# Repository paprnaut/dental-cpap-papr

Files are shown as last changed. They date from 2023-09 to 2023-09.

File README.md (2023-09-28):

# Dental CPAP PAPR

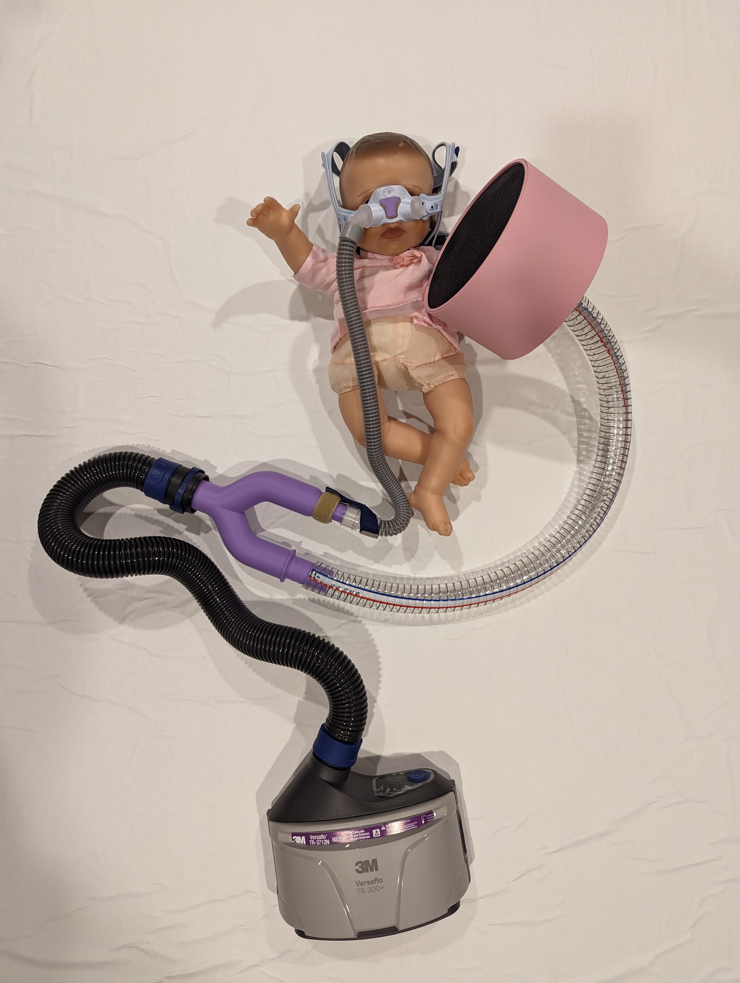
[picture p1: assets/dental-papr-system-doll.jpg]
System photo

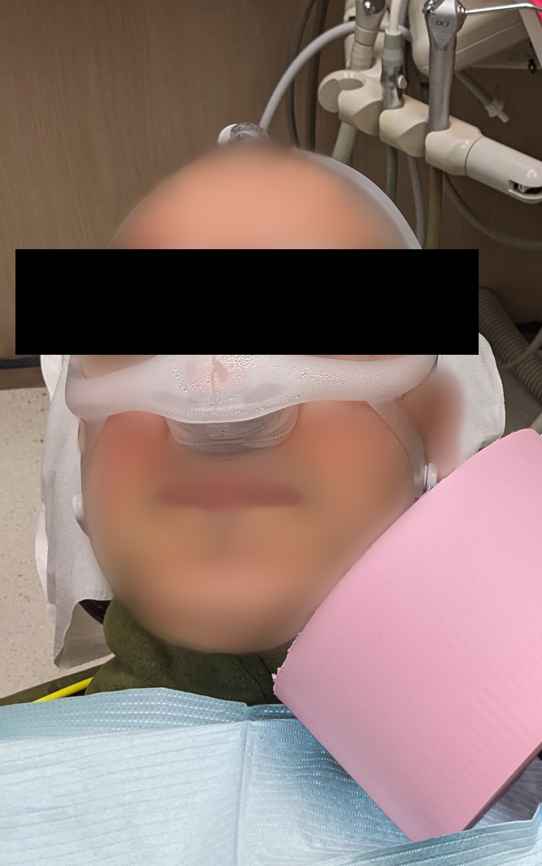
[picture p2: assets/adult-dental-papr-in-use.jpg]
In use photo photo


***Important Disclaimer: This is a prototype device, offered free-of-charge as a public service, and no claim, guarantee, or warranty of performance or suitablity for any purpose is offered or implied.  This device has not been independently certified or approved.  Use of this design or any derivatives thereof is entirely at your own risk.  By using any of these materials, you acknowledge that you have read and understood the Disclaimer at the end of this document.  Please do not use these materials if you do not understand and accept these risks.***

## Bill of Materials

**Printed Parts**
| Item | Quantity | Notes |
| ---- | -------- | ----- |
| Dental PAPR - Child CPAP Hole Plug.stl | 1 | To plug holes in Pixi nasal pad. Print for child version only. |
| Dental PAPR - LaminarNozzleBody-Wide.stl | 1 | Handheld wand to blow clean air over the mouth and face. |
| Dental PAPR - LaminarNozzleFitting-Female-Short.stl | 1 | Nut for handheld wand. |
| Dental PAPR - LaminarNozzleFitting-Short.stl | 1 | Hose fitting for handheld wand. |
| Dental PAPR - MeshHolderSpacer-Wide.stl | 2 | Hoop frames. Glue screen door material onto these to hold straws in place. |
| Dental PAPR - NozzleFlowReducer d0,50.stl | 1 | Part with 0,5" opening inserts into hose fitting on Y-splitter to reduce flow to the handheld wand to improve flow to the CPAP. Tested for adult version only. |
| Dental PAPR - TR300 Y Adapter - Adult.stl | 1 | Y-splitter / adapter. Print for adult version only. |
| Dental PAPR - TR300 Y Adapter - Child.stl | 1 | Y-splitter / adapter. Print for child version only. |
| Dental PAPR - v1 tr300 y-splitter.3mf | 1 | Y-splitter / adapter for v1 with adjustable valves only. |
| Dental PAPR - v1 1in pipe to CPAP adapter.3mf | 1 | CPAP hose adapter for v1 with adjustable valves only. |
| Dental PAPR - Dental PAPR v1 - 1in pipe to 1in hose barb.3mf | 1 | 1" hose adapter for v1 with adjustable valves only. |

**Purchased Parts**
| Item | Quantity | Example Source | Notes |
| ---- | --------:| -------------- | ----- |
| 3M TR-302N+ PAPR Unit | 1 | https://www.3m.com/3M/en_US/p/d/v100559007/ | Available in 3M™ Versaflo™ Easy Clean PAPR Kit TR-300N+ ECK 1 EA/Case Part Number 1334259 |
| 3M BT 30 Length Adjusting Breathing Tube | 1 | https://www.3m.com/3M/en_US/p/d/v100559007/ | Available in 3M™ Versaflo™ Easy Clean PAPR Kit TR-300N+ ECK 1 EA/Case Part Number 1334259 |
| 3M TR-332 High Capacity Battery | 1 | https://www.3m.com/3M/en_US/p/d/v100559007/ | Available in 3M™ Versaflo™ Easy Clean PAPR Kit TR-300N+ ECK 1 EA/Case Part Number 1334259 |
| 3M TR-3712N HE Filter | 1 | https://www.3m.com/3M/en_US/p/d/v100559007/ | Available in 3M™ Versaflo™ Easy Clean PAPR Kit TR-300N+ ECK 1 EA/Case Part Number 1334259 |
| 3M TR-341N Battery Charger Kit | 1 | https://www.3m.com/3M/en_US/p/d/v100559007/ | Available in 3M™ Versaflo™ Easy Clean PAPR Kit TR-300N+ ECK 1 EA/Case Part Number 1334259 |
| Plastic Drinking Straws | 500 | https://www.amazon.com/dp/B08TDTK58T | Two sets of 250 will leave lots left over. Cut to 2.25" length |
| Fiberglass Screen Door Replacement Mesh | 1 | https://www.amazon.com/dp/B093YP514T | Only need two 6" circles, so this will leave A LOT left over |
| Scotch-Brite Scour Pads | 2 | https://www.amazon.com/dp/B001KYQBX0 | Eaxample is a pack of eight. Only two are needed to make a 6" circle |
| DreamWisp Nasal CPAP Mask Fit Pack Kit | 1 | https://www.1800cpap.com/dreamwisp-nasal-cpap-mask-fitpack-kit?quantity=1&add-headgear=Yes | For adult version only |
| Universal CPAP Tubing Hose 6' | 1 | https://www.1800cpap.com/cpap-tubing-hose-6ft | For adult version only |
| ResMed Pixi Pediatric Nasal Mask Frame System with Standard System & Headgear | 1 | https://www.resmed.com/en-us/sleep-apnea/cpap-parts-support/sleep-apnea-full-products-list/cpap-masks/pixi/# | For child version only |
| 1" ID Flexible Tubing | 2' | https://www.amazon.com/gp/product/B099F4LMWF | 1.5 to 2 feet are sufficient. This example has reinforcing wire which in hindsight is unnecessary and difficult to work with. |
| True Union Ball Valve 1" with Full Port (2-Pack) | 1 | https://www.amazon.com/gp/product/B09KPBMF46/ | Full-flow valves. Seem well-built but are heavy. For v1 only. |

## Assembly
1. Print required parts. These parts were printed in standard PLA on a filament-style 3D printer.
2. Cut straws to 2.25" length.
3. Slide threaded side of LaminarNozzleFitting-Short into the LaminarNozzleBody-Wide
4. Screw the LaminarNozzleFitting-Female-Short onto the LaminarNozzleFitting-Short to hold in in place
5. Cut two 6" circles of screen door material and superglue them onto the MeshHolderSpacer-Wide hoops.
7. Cut two semicircles out of Scotch-Brite to make a 6" diameter circle and glue it into one of the hoops.
8. Slide the hoop with the scotch-brite (scouring pad side down) into the LaminarNozzleBody-Wide until it rests against the lip.
9. Load the MeshHolderSpacer-Wide with cut plastic straws.
10. Slide the other hoop into the top and glue in place with superglue.
11. Place the flow reducer into the hose fitting on the Y-splitter (improves performance on adult version. Pediatric flow reducers untested).
12. Cut the 1" ID hose to length and attach to the hose fitting on the MeshHolderSpacer-Wide and the Dental PAPR - TR300 Y Adapter.
13. Connect the CPAP tubing to the connector on the Y Adapter. For the child version, it can be helpful to add a band of velcro to the "fingers" on the connector to hook up with the velcro pad on the eleastic band on the Pixi.
14. 3M BT 30 Length Adjusting Breathing Tube to the fitting at the base of the Y-Adapter

## Disclaimer
**Regulatory Notice**

This product has not been cleared for medical use by the U.S. Food and Drug Administration. This product has not been evaluated for the prevention of specific diseases or infections, the filtering of surgical smoke or plumes, the filtering of specific amounts of viruses or bacteria, or the killing or reduction of the amount of viruses, bacteria or fungi. This product is intended for use by a single user. Performance is not guaranteed in any way. No passive protection is provided for the mouth. What limited protection for the mouth may be available requires careful placement and use of the handheld device.

**Liability Notice**

By using this product, the end user assumes all risks associated with its use, including the voiding of manufacturers’ warranties of devices with which the product is used, and agrees to hold harmless and waive any claims against any persons or companies which may have contributed to the design and specifications. EXCEPT WHERE SPECIFICALLY PROHIBITED BY LAW, NO WARRANTIES OF ANY KIND ARE OFFERED FOR THE PRODUCT DESIGN AND SPECIFICATIONS, INCLUDING WARRANTIES OF NON-INFRINGEMENT AND FITNESS FOR A PARTICULAR PURPOSE.

**Intellectual Property License**

Individuals and organizations are free to use, copy, and share this design and specifications, including for commercial manufacture, without payment of any fees or charges, but may not assert ownership in the design and specifications.

**Notice to Manufacturers**

Individuals or organizations that manufacture products utilizing this design and specifications are responsible for any federal or state regulatory requirements that apply to the manufacture of products intended for medical use, and are responsible for informing health care providers to which the product is supplied that they are responsible for decisions regarding appropriate personal protective equipment for their personnel. The distribution or sale of products manufactured using this design and specifications must include the Regulatory Notice and the Liability Notice as set forth above displayed prominently on packaging and marketing materials, as well as any information required by the FDA or other governmental authorities.

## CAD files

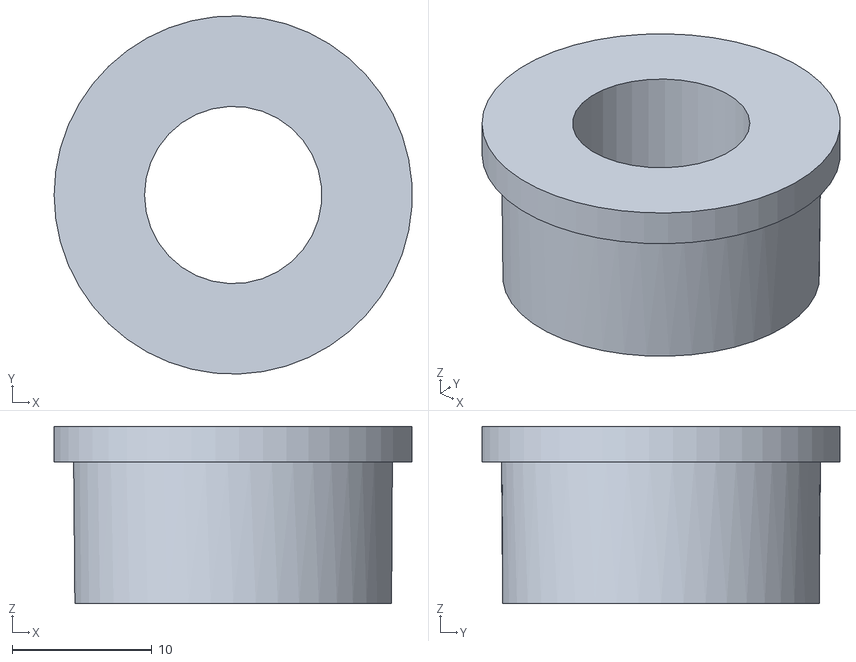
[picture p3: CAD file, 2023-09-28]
Dental PAPR - NozzleFlowReducer d0,50.stl
25.6 x 25.6 x 12.7

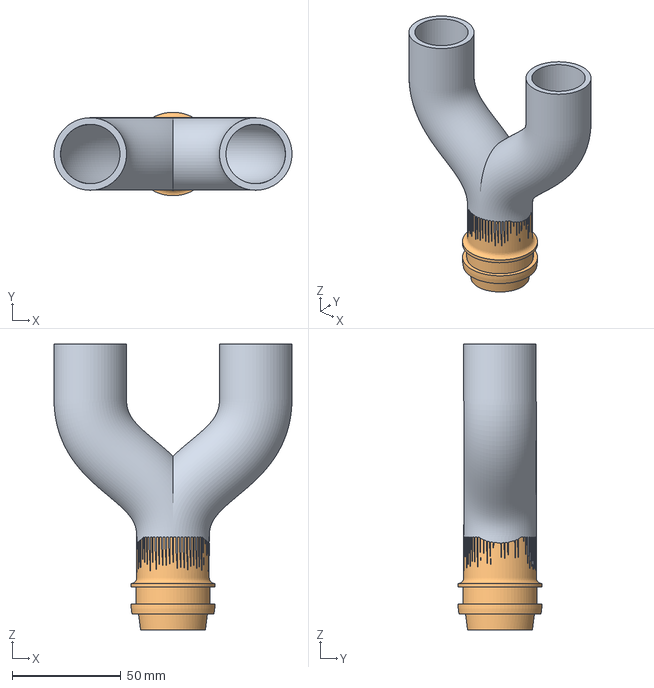
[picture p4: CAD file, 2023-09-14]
Dental PAPR v1 - tr300 y-splitter.3mf
109.6 x 38.5 x 131.7 mm
TR300 to 1" PVC

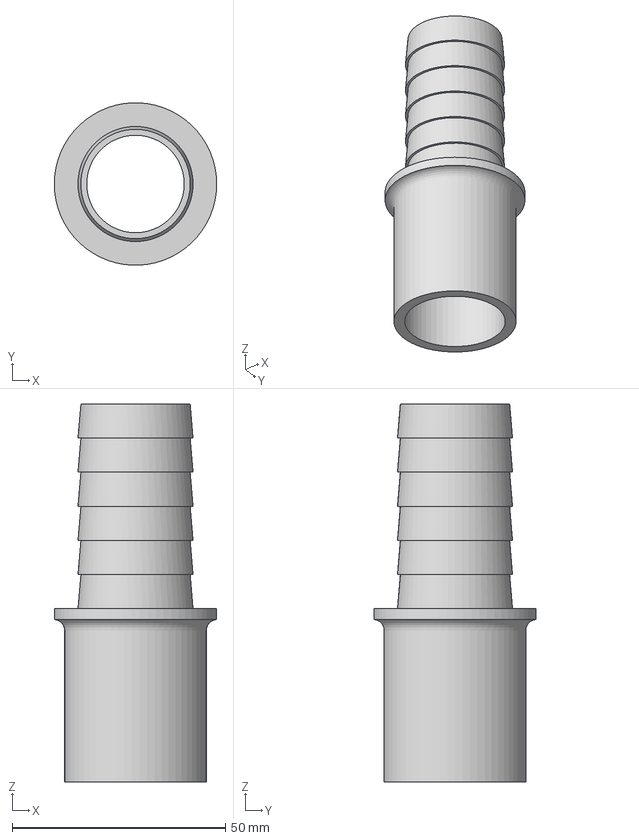
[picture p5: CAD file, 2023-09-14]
Dental PAPR v1 - 1in pipe to 1in hose barb.3mf
38.1 x 38.1 x 88.6 mm

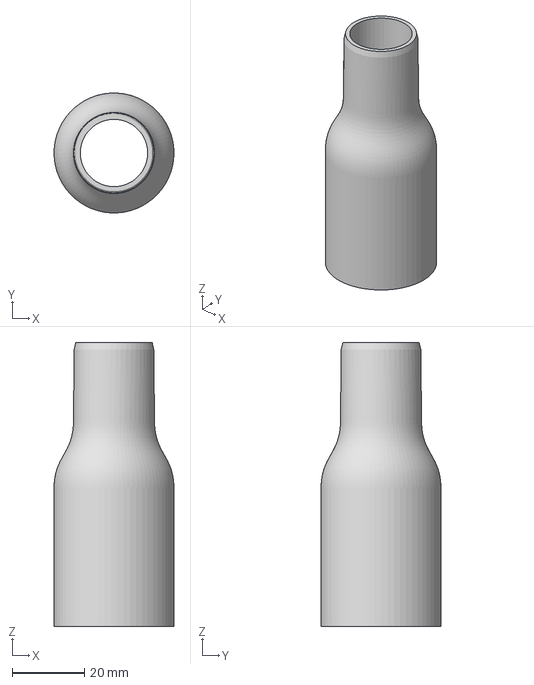
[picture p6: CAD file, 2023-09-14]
Dental PAPR v1 - 1in pipe to CPAP adapter.3mf
33.3 x 33.2 x 78.7 mm

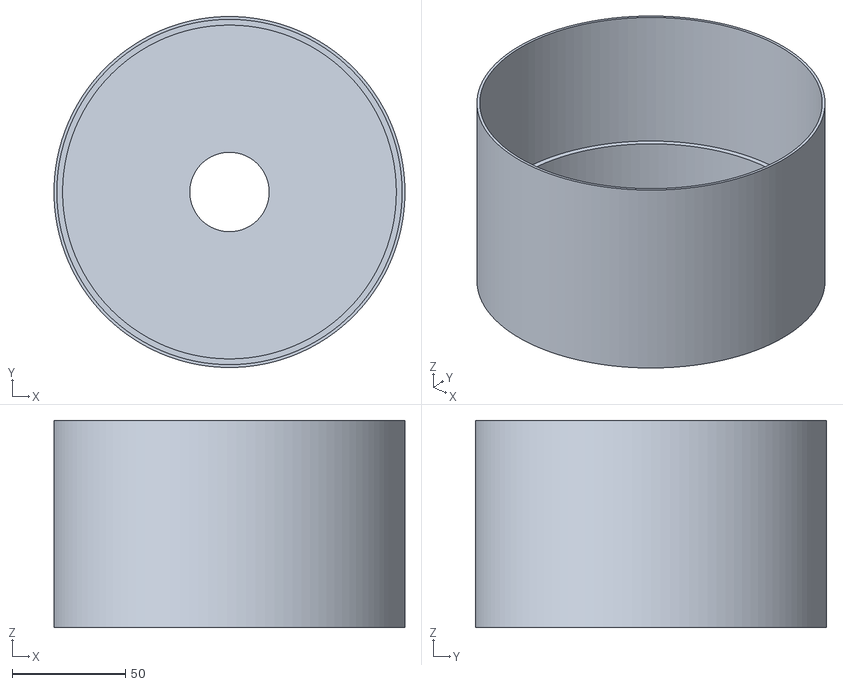
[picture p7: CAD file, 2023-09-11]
Dental PAPR - LaminarNozzleBody-Wide.stl
154.9 x 154.9 x 91.4

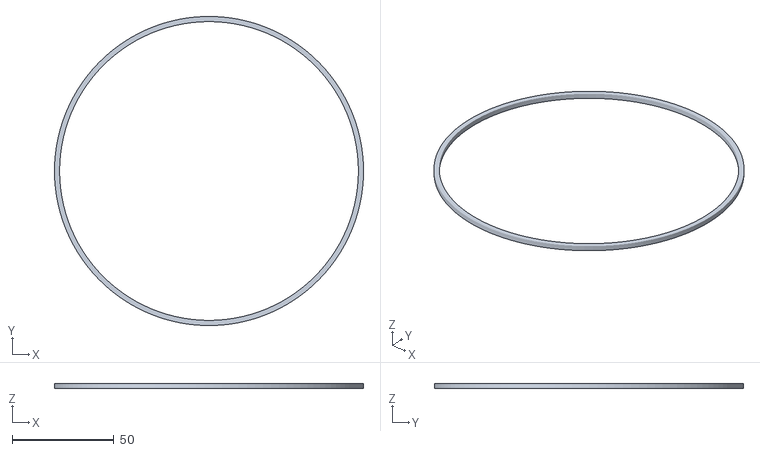
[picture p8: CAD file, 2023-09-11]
Dental PAPR - MeshHolderSpacer-Wide.stl
151.9 x 151.8 x 2.54

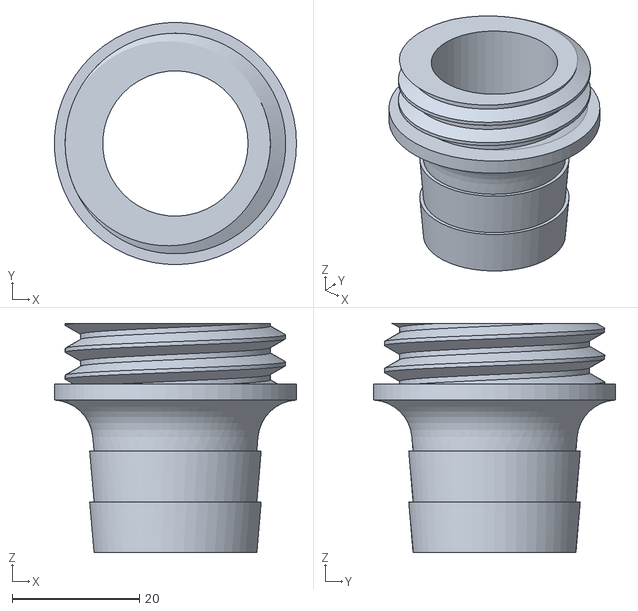
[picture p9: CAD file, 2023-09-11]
Dental PAPR - LaminarNozzleFitting-Short.stl
38.1 x 38.1 x 36.1

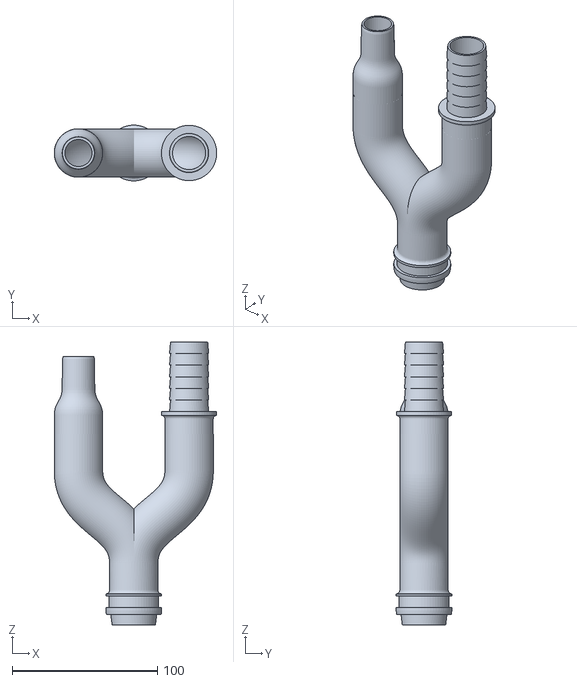
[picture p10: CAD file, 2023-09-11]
Dental PAPR - TR300 Y Adapter - Adult.stl
111.9 x 38.4 x 194.9

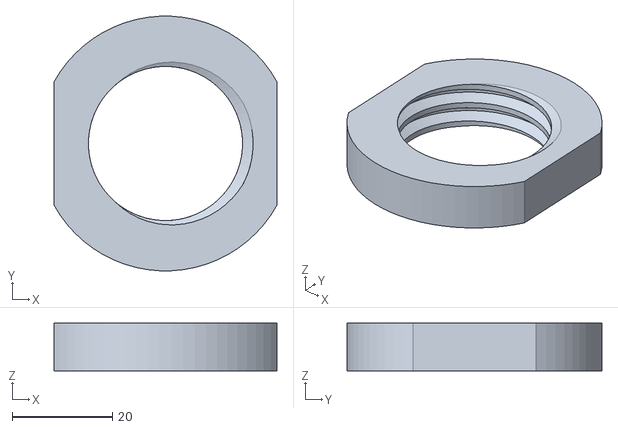
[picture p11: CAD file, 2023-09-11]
Dental PAPR - LaminarNozzleFitting-Female-Short.stl
44.4 x 50.7 x 9.52

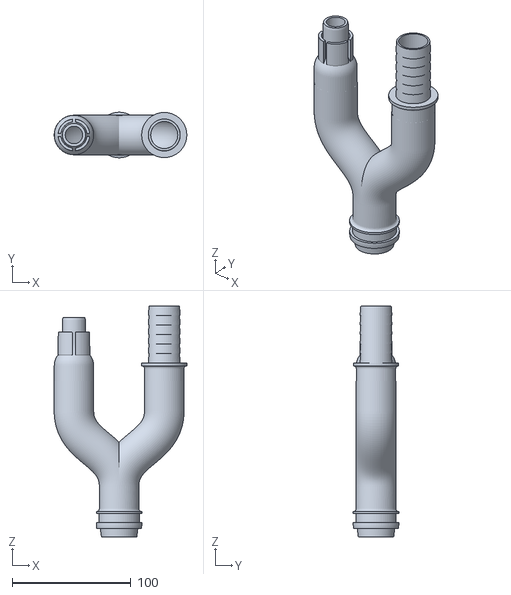
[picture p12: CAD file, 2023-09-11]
Dental PAPR - TR300 Y Adapter - Child.stl
111.9 x 38.4 x 194.9

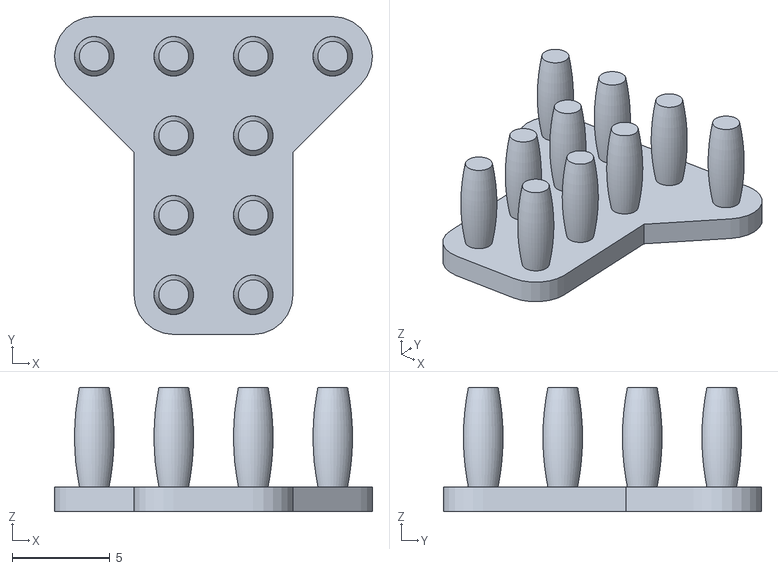
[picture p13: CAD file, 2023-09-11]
Dental PAPR - Child CPAP Hole Plug.stl
16.3 x 16.3 x 6.35

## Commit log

2023-09-11 Add files via upload
    Initial CAD file upload
    [Dental PAPR - Child CPAP Hole Plug.stl, Dental PAPR - LaminarNozzleBody-Wide.stl, Dental PAPR - LaminarNozzleFitting-Female-Short.stl, Dental PAPR - LaminarNoz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]
2023-09-14 Add files via upload
    Added v1 3D print files
    [Dental PAPR v1 - 1in pipe to 1in hose barb.3mf, Dental PAPR v1 - 1in pipe to CPAP adapter.3mf, Dental PAPR v1 - tr300 y-splitter.3mf]
2023-09-28 Add files via upload
    Added flow reducer/balancer, which restricts the flow to the handheld wand. A diameter of 0.500" tested best with Portacount 8020A.
    [Dental PAPR v51 - NozzleFlowReducer d0,50.3mf]
2023-09-28 Delete Dental PAPR v51 - NozzleFlowReducer d0,50.3mf
    Upload error. Will replace with STL
    [Dental PAPR v51 - NozzleFlowReducer d0,50.3mf]
2023-09-28 Add files via upload
    Flow reducer (1/2" dimeter orifice) to direct more air to mask. Improves performance of adult version.
    [Dental PAPR - NozzleFlowReducer d0,50.stl]
